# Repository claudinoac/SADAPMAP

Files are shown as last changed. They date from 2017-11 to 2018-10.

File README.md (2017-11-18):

# <h1> SADAMAP </h1>
<h2> Sistema de Aquisição de Dados para Análise de Materiais em Altas Pressões </h2>

<h3> Pré Requisitos de Instalação: </h3> 

<h4> Python 3.2+: </h4>
<ul> 
	<li> https://www.python.org/downloads/ </li>
</ul>
<h4>  </h4>
<h4> Bibliotecas Python: </h4>
<ul> 
	<li>  PyQtGraph: http://www.pyqtgraph.org/ </li>
	<li>  Numpy: http://www.numpy.org/ </li>
	<li>  PySerial: https://github.com/pyserial/pyserial </li>
	<li>  PyQt5: https://www.riverbankcomputing.com/software/pyqt/download5
</ul>

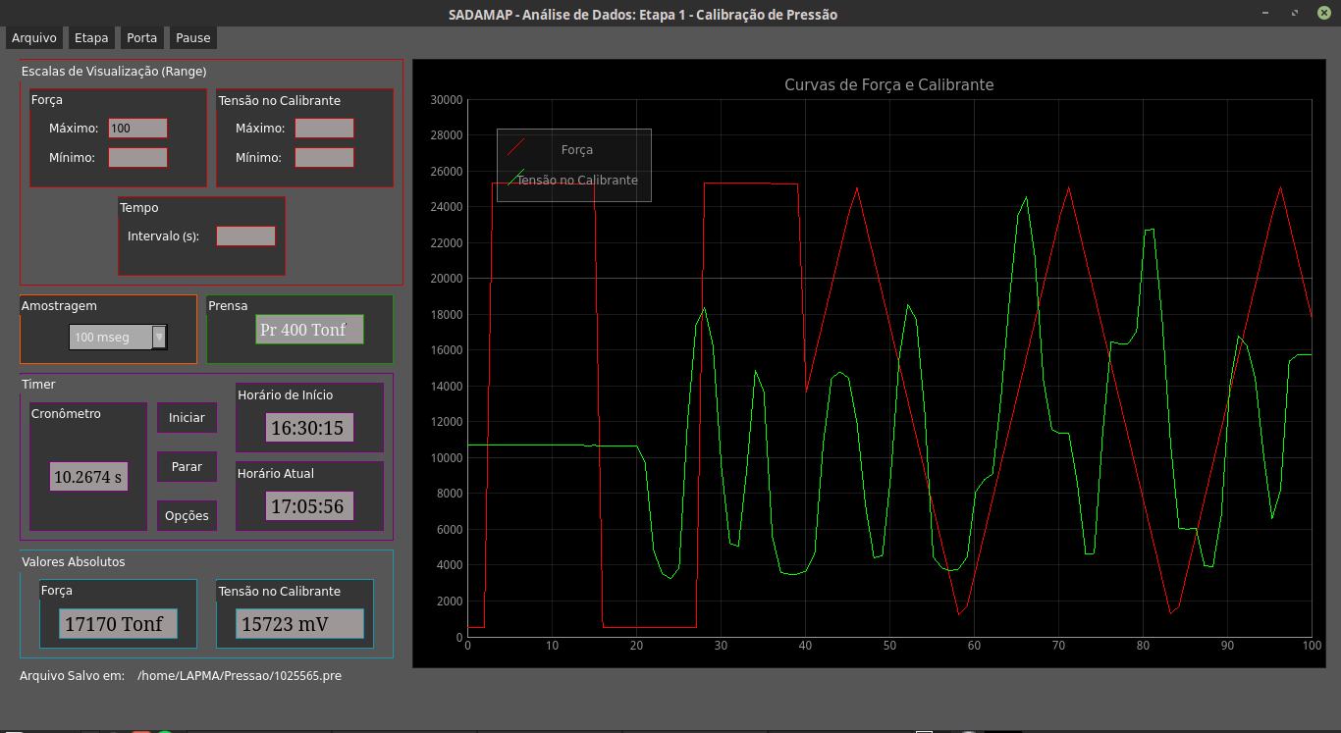
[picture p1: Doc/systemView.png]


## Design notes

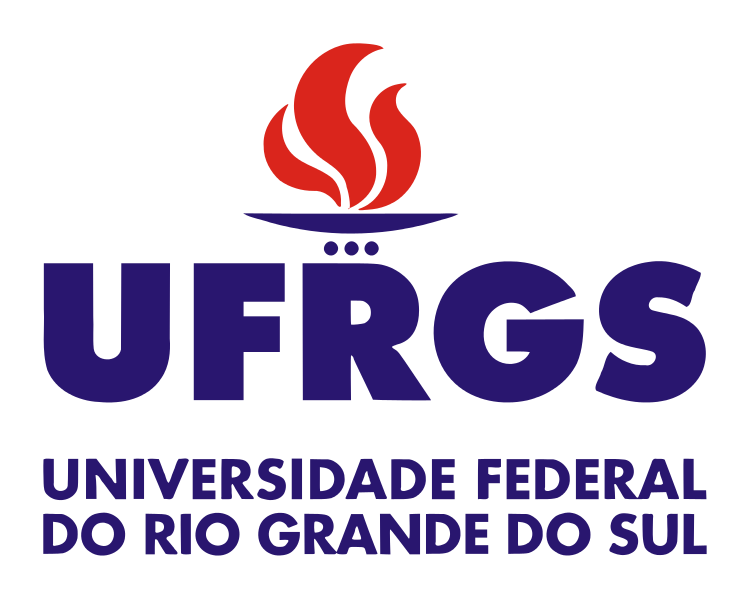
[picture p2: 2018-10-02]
Interface/Resources/750px-Ufrgs.svg.png

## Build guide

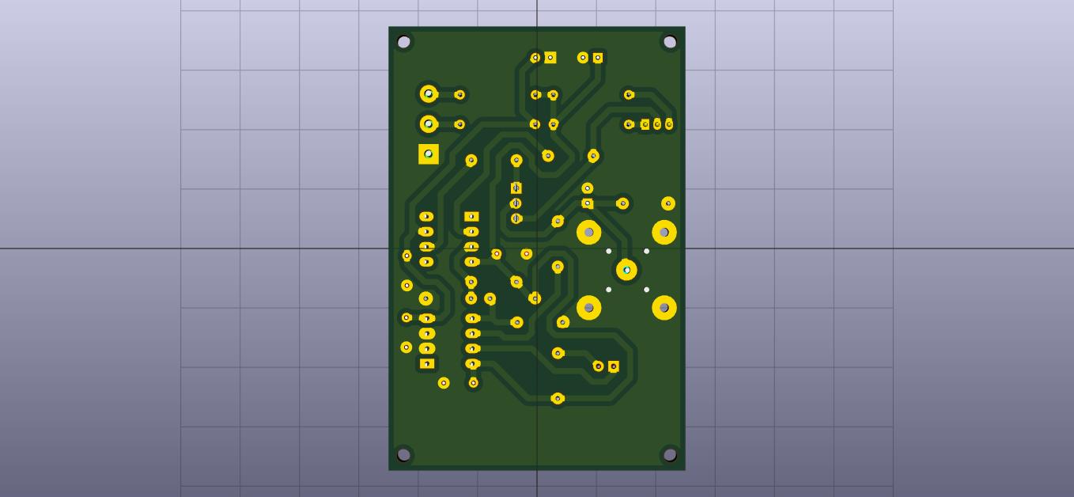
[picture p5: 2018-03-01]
Circuits/I_SOURCE/Fabrication Files/I_SOURCE_BACK.jpg

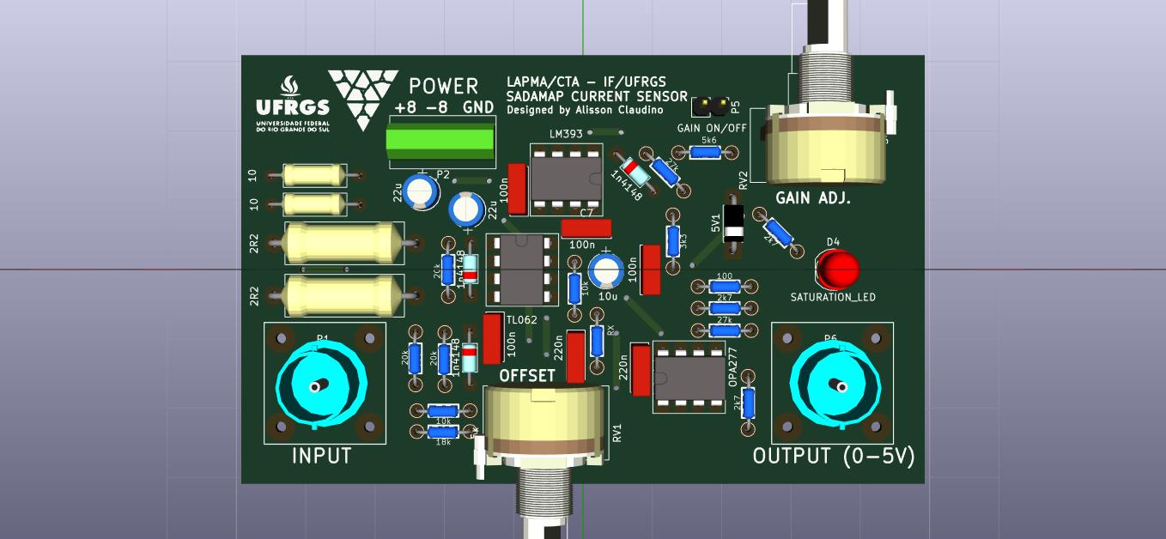
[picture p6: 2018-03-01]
Circuits/I_AMP/Fabrication Files/I_AMP_FRONT.jpg

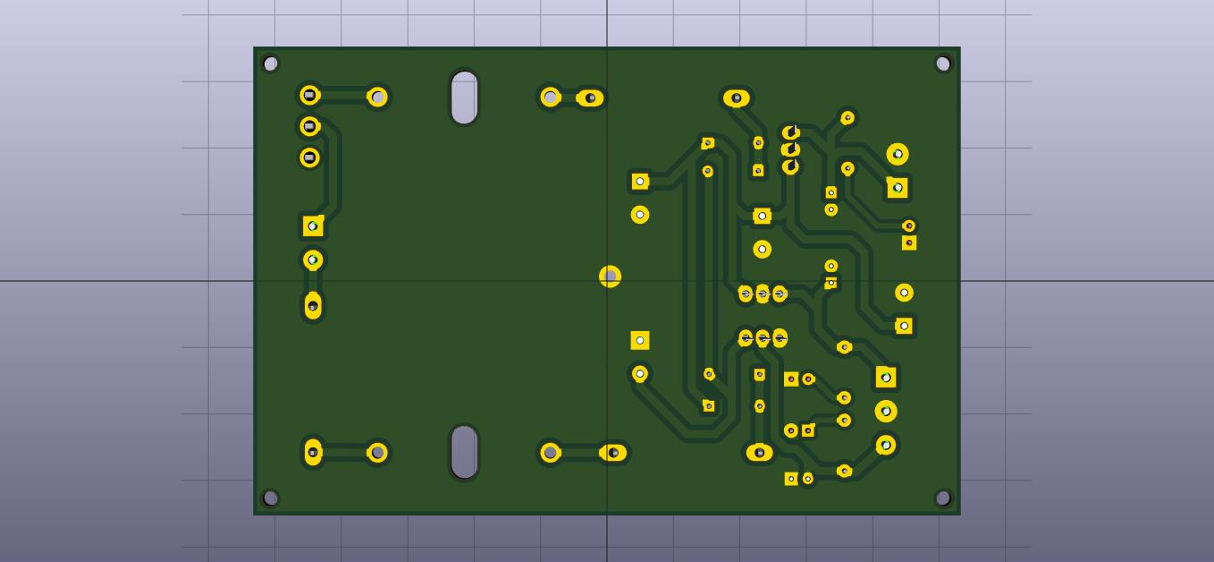
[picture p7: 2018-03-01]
Circuits/P_SUPPLY/Fabrication Files/P_SUPPLY_BACK.jpg

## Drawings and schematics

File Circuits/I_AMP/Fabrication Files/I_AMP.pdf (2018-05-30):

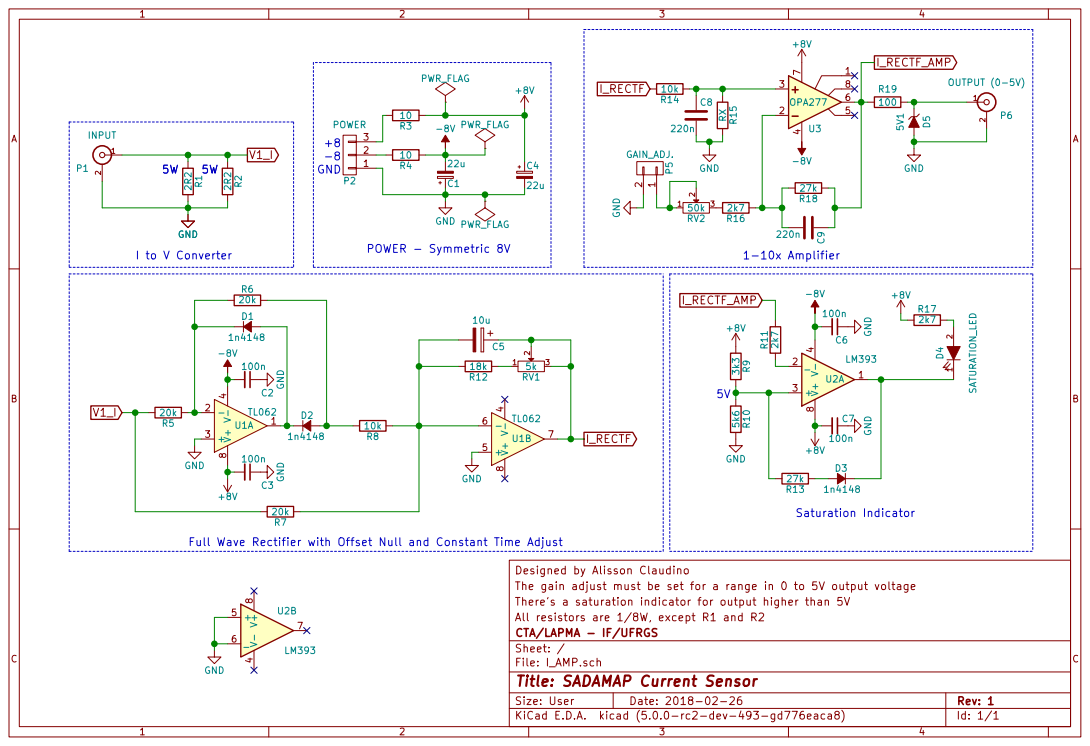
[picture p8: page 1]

Designed by Alisson Claudino GND

Full Wave Rectifier with Offset Null and Constant Time Adjust

The gain adjust must be set for a range in 0 to 5V output voltage
There's a saturation indicator for output higher than 5V
All resistors are 1/8W, except R1 and R2
File: I_AMP.sch Sheet: / CTA/LAPMA - IF/UFRGS

Id: 1/1 Title: SADAMAP Current Sensor

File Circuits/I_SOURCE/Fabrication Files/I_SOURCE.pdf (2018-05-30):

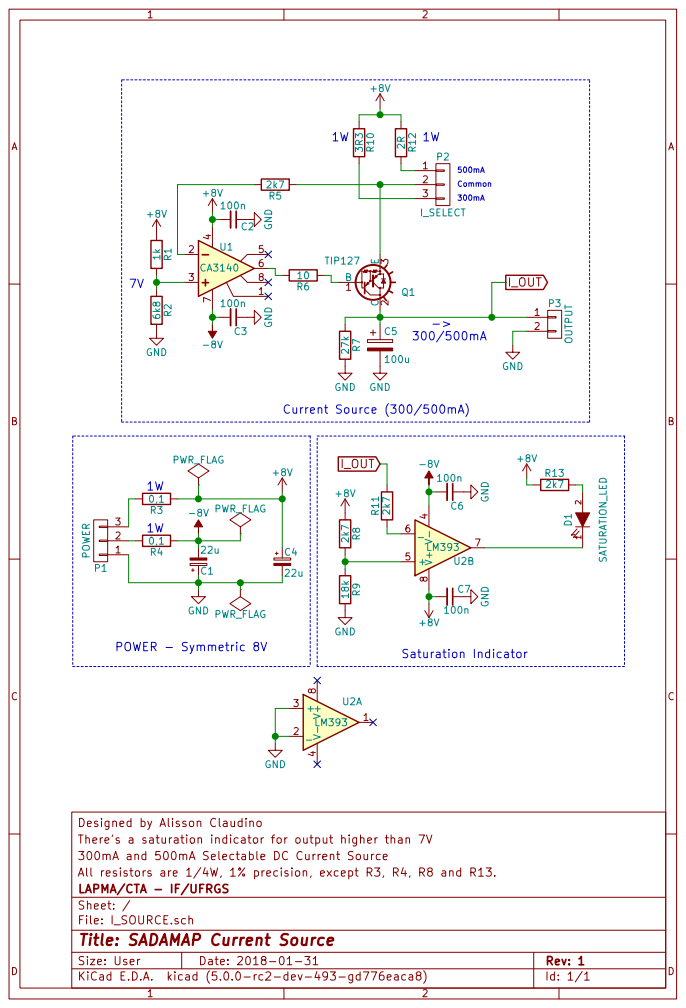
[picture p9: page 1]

Designed by Alisson Claudino
All resistors are 1/4W, 1% precision, except R3, R4, R8 and R13. 300mA and 500mA Selectable DC Current Source There's a saturation indicator for output higher than 7V

File: I_SOURCE.sch Sheet: / LAPMA/CTA - IF/UFRGS

Id: 1/1 Title: SADAMAP Current Source

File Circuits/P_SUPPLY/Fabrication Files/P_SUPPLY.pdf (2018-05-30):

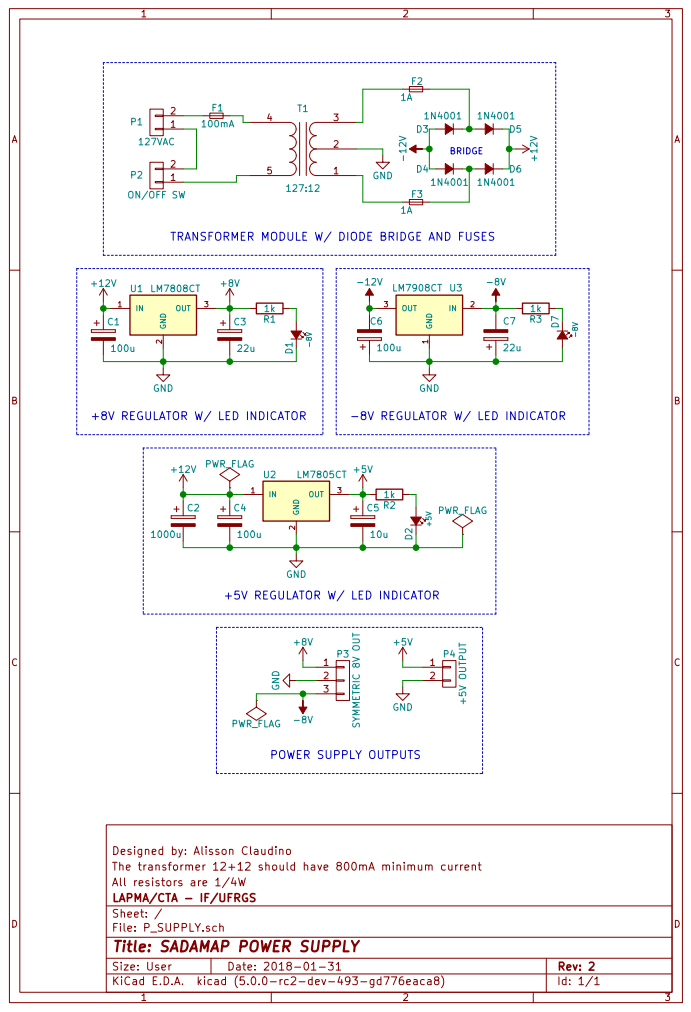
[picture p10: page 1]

1k TRANSFORMER MODULE W/ DIODE BRIDGE AND FUSES

The transformer 12+12 should have 800mA minimum current Designed by: Alisson Claudino

All resistors are 1/4W
File: P_SUPPLY.sch Sheet: / LAPMA/CTA - IF/UFRGS

Id: 1/1 Title: SADAMAP POWER SUPPLY

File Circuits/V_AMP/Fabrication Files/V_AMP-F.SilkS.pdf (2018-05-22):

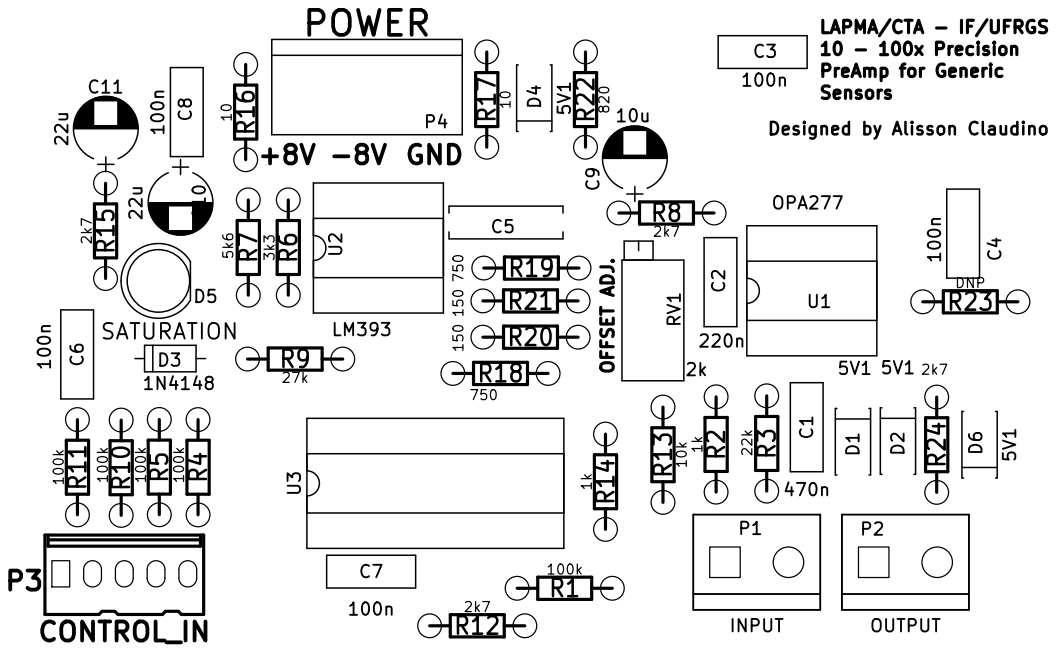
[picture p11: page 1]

LAPMA/CTA - IF/UFRGS
10 - 100x Precision PreAmp for Generic Sensors

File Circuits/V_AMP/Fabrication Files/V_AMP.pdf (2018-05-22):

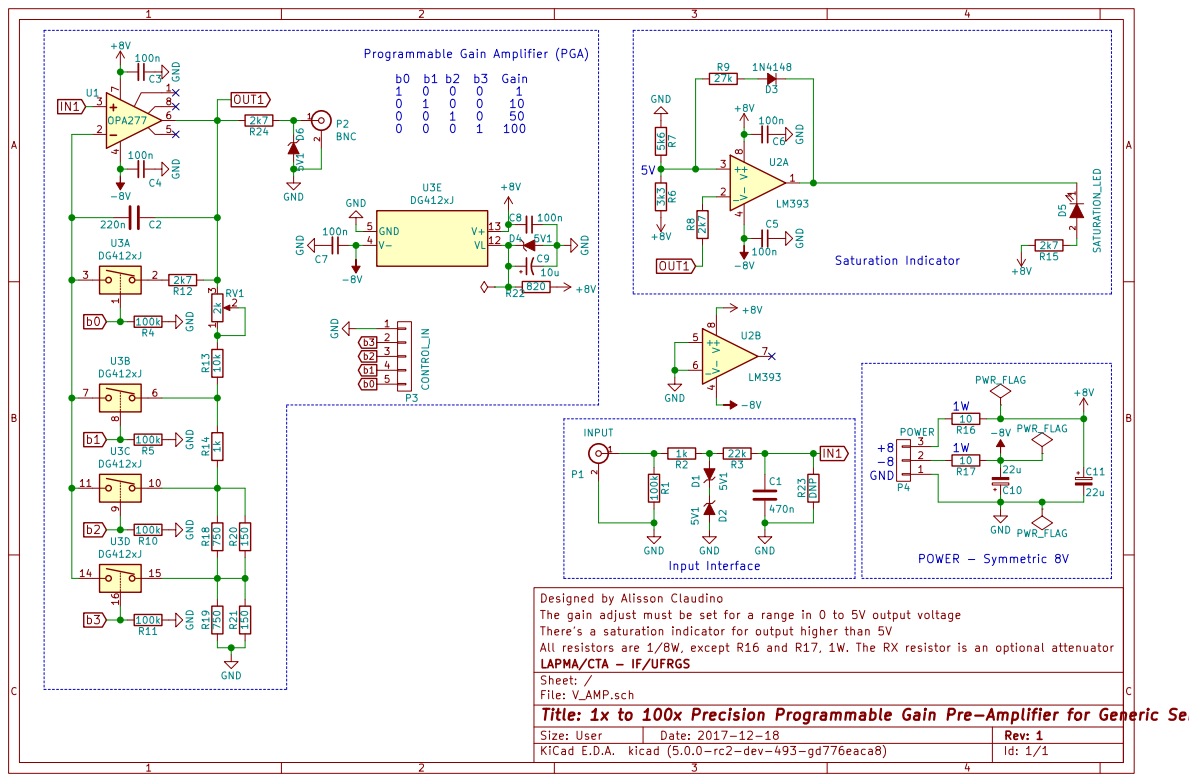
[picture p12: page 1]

Designed by Alisson Claudino
The gain adjust must be set for a range in 0 to 5V output voltage
There's a saturation indicator for output higher than 5V
All resistors are 1/8W, except R16 and R17, 1W. The RX resistor is an optional attenuator
LAPMA/CTA - IF/UFRGS
Sheet: /
File: V_AMP.sch
Title: 1x to 100x Precision Programmable Gain Pre-Amplifier for Generic Sensors
KiCad E.D.A. kicad (5.0.0-rc2-dev-493-gd776eaca8)

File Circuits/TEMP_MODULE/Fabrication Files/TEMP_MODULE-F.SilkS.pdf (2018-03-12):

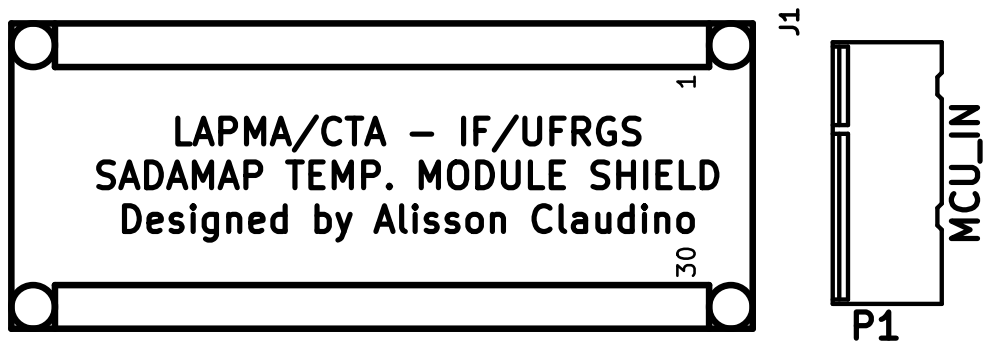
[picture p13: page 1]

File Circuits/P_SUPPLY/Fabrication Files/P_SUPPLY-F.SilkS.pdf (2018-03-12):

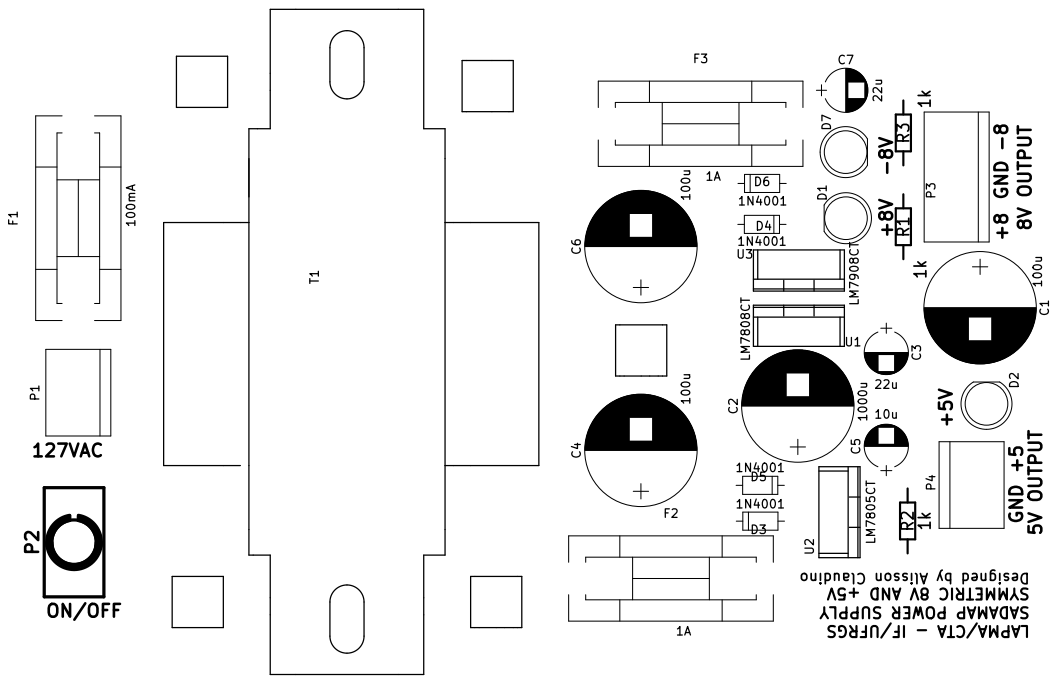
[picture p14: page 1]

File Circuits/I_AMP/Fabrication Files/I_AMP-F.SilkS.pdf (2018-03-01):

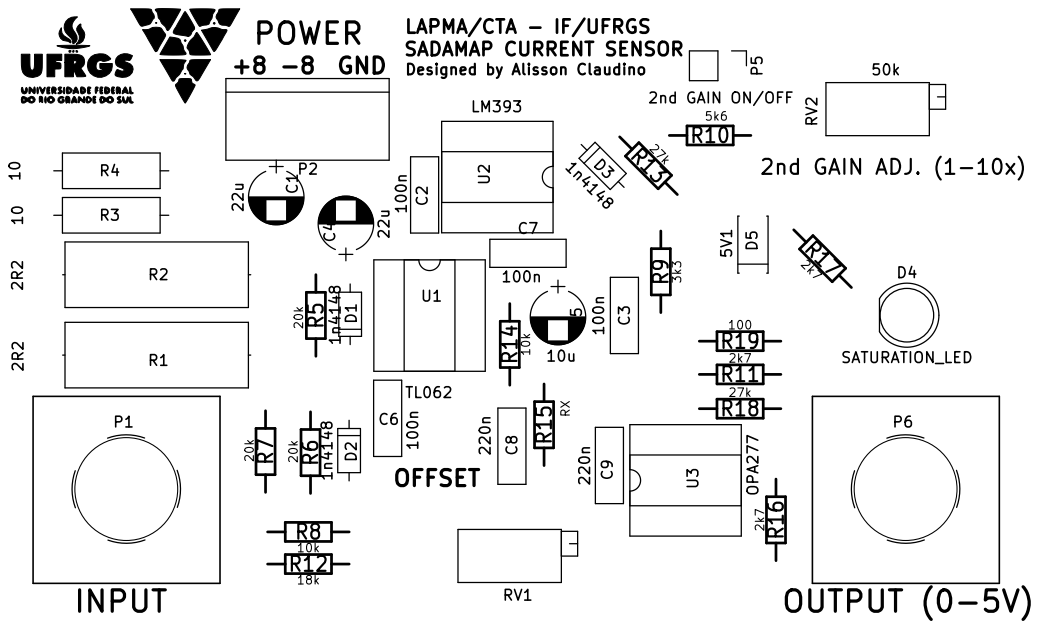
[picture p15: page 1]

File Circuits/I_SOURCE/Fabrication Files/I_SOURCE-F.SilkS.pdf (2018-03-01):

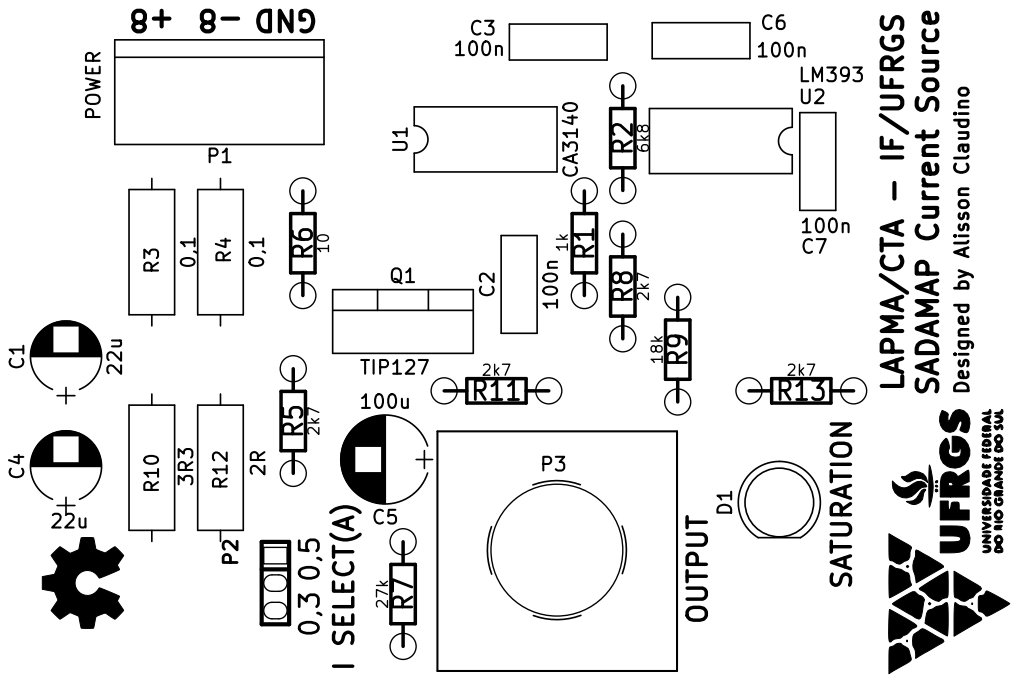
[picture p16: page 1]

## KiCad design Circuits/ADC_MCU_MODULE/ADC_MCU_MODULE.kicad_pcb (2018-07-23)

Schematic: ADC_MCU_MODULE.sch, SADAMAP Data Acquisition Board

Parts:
C1: 22u; C_Radial_D5_L6_P2.5
C2, C3, C4, C5, C6, C7, C8, C9: 100n; C_Rect_L7_W2.5_P5
J1: Arduino_Nano_Header; arduino_nano_header
P1: POWER; bornier2
P2, P3, P4, P5, P6, P7, P8, P9: BNC; bornier2
P10: TEMP_MODULE_OUT; kk100_22-23-2061
P11: V_AMP SEL CH-B; kk100_22-23-2051
P12: V_AMP SEL CH-A; kk100_22-23-2051
P13: V_AMP SEL CH-C; kk100_22-23-2051
R1: 10R; R_Axial_DIN0309_L9.0mm_D3.2mm_P12.70mm_Horizontal
R2, R3, R4, R5, R6, R7, R8, R9: 47k; RC03
U1, U2: ADS1115

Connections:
+5V: C1.1, J1.27 (5V), J1.30 (VIN), P10.2, R1.2, U1.1 (VCC), U2.1 (VCC), U2.5 (ADDR)
ADC1: C2.1, R2.1, U1.7 (A0)
ADC2: C5.1, R5.1, U1.8 (A1)
ADC3: C3.1, R3.1, U1.9 (A2)
ADC4: C4.1, R4.1, U1.10 (A3)
ADC5: C6.1, R6.1, U2.7 (A0)
ADC6: C7.1, R7.1, U2.8 (A1)
ADC7: C8.1, R8.1, U2.9 (A2)
ADC8: C9.1, R9.1, U2.10 (A3)
GND: C1.2, C2.2, C3.2, C4.2, C5.2, C6.2, C7.2, C8.2, C9.2, J1.4 (GND), J1.29 (GND), P1.1, P2.2 (Ext), P3.2 (Ext), P4.2 (Ext), P5.2 (Ext), P6.2 (Ext), P7.2 (Ext), P8.2 (Ext), P9.2 (Ext), P10.1, P11.1, P12.1, P13.1, U1.2 (GND), U1.5 (ADDR), U2.2 (GND)
MISO: J1.15 (D12/MISO), P10.4
MOSI: J1.14 (D11/MOSI), P10.5
unnamed: P1.2, R1.1
unnamed: P2.1 (In), R2.2
unnamed: P3.1 (In), R3.2
unnamed: P4.1 (In), R4.2
unnamed: P5.1 (In), R5.2
unnamed: P6.1 (In), R6.2
unnamed: P7.1 (In), R7.2
unnamed: P8.1 (In), R8.2
unnamed: P9.1 (In), R9.2
SCK: J1.16 (SCK/D13), P10.6
SCL: J1.24 (A5), U1.3 (SCL), U2.3 (SCL)
SDA: J1.23 (A4), U1.4 (SDA), U2.4 (SDA)
VA0: J1.19 (A0), P12.5
VA1: J1.20 (A1), P12.4
VA2: J1.21 (A2), P12.3
VA3: J1.22 (A3), P12.2
VB0: J1.5 (D2/INT0), P11.5
VB1: J1.6 (D3/INT1), P11.4
VB2: J1.7 (D4/T0), P11.3
VB3: J1.8 (D5/T1), P11.2
VC0: J1.9 (D6/AIN0), P13.5
VC1: J1.10 (D7/AIN1), P13.4
VC2: J1.11 (D8/ICP), P13.3
VC3: J1.12 (D9/0C1), P13.2
~CS: J1.13 (D10/SS), P10.3

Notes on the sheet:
INPUTS WITH ANTI-ALIASING LP FILTER
ADS1115 I2C MODULES The ADC_A has 0x48 I2C address and ADC_B, 0x49
POWER INPUT The 10R resistor is used as a fuse and the 22u capacitor is used as a filter
ARDUINO NANO MODULE
ADC_A
ADC_B
MAX31856 Temperature Module Header
Digital Voltage Amplifier Controls

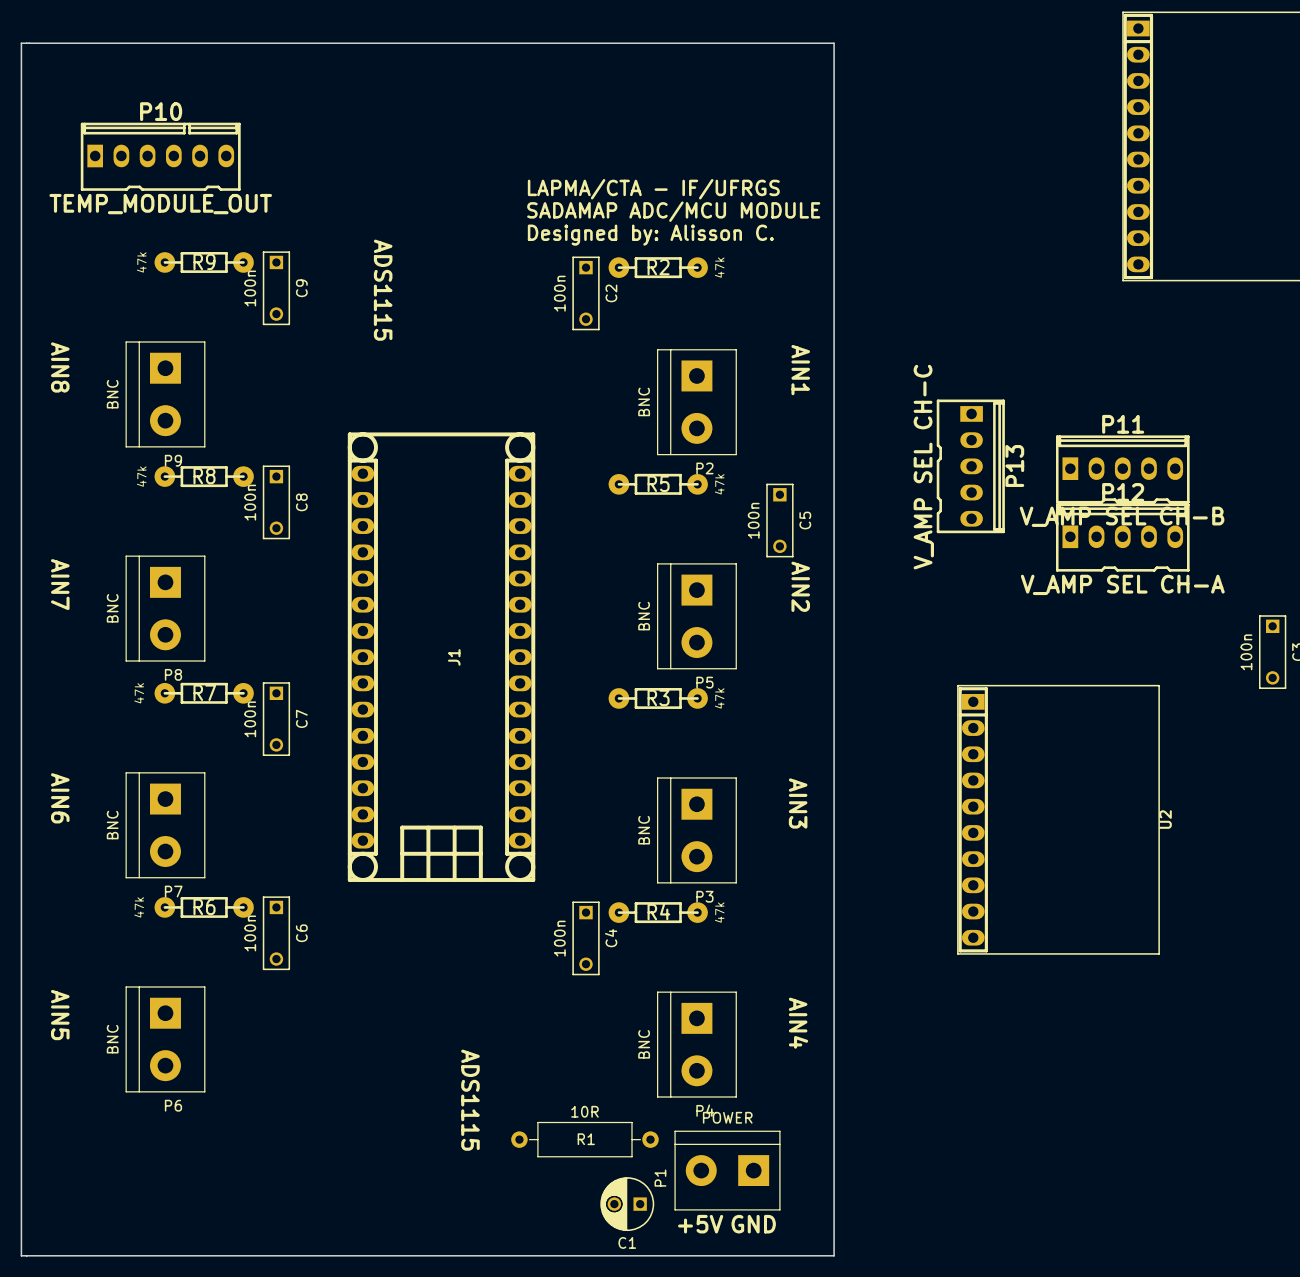
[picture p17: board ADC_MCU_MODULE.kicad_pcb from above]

Board: 2 copper layers, 78.8 x 117.5 mm, 34 parts (0 on the bottom side), 37 nets.

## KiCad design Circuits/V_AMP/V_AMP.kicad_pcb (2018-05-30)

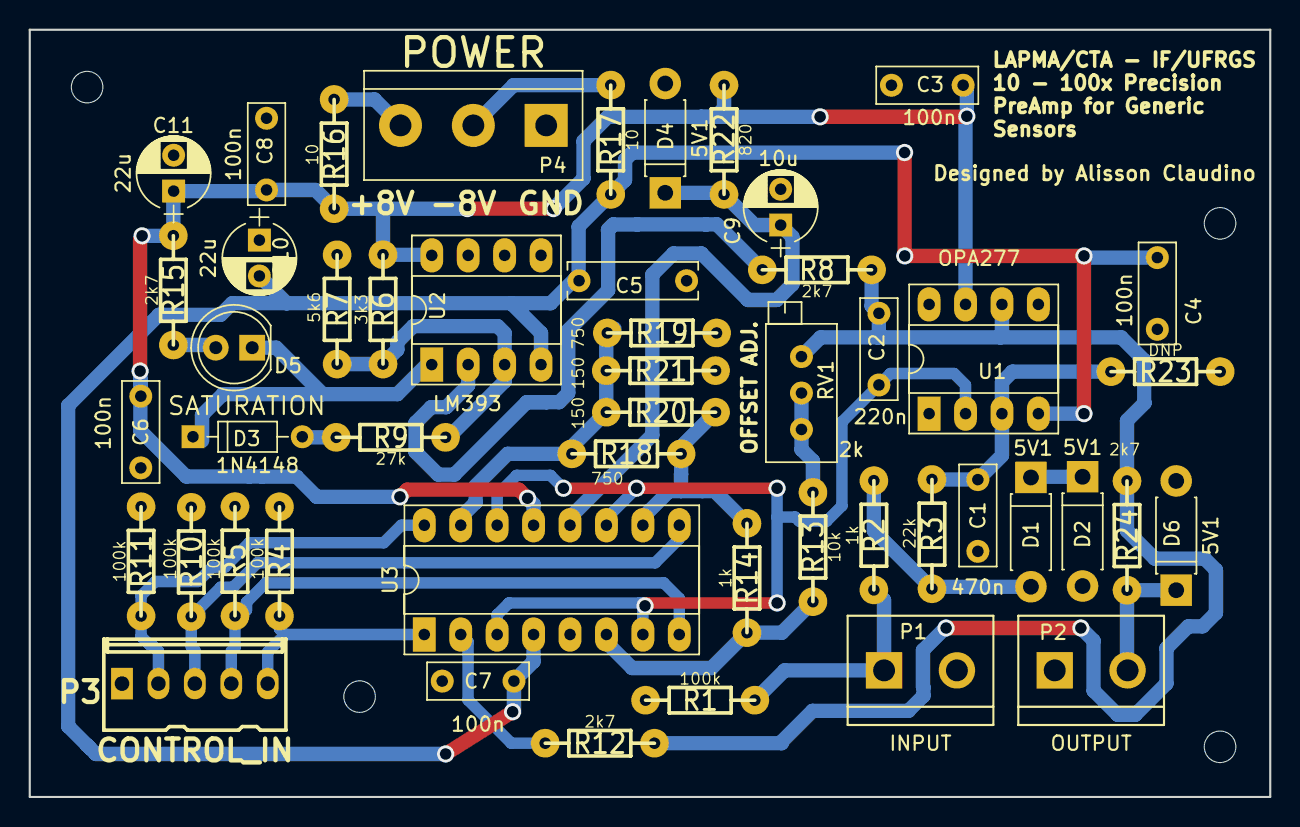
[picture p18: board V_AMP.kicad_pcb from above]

Board: 2 copper layers, 86.5 x 53.5 mm, 49 parts (0 on the bottom side), 27 nets.

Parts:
C1: 470n; C_Rect_L7.0mm_W2.5mm_P5.00mm
C2: 220n; C_Rect_L7.0mm_W2.5mm_P5.00mm
C3, C4, C6, C7, C8: 100n; C_Rect_L7.0mm_W2.5mm_P5.00mm
C5: 100n; C_Rect_L9.0mm_W2.5mm_P7.50mm_MKT
C9: 10u; CP_Radial_D5.0mm_P2.50mm
C10, C11: 22u; CP_Radial_D5.0mm_P2.50mm
D1, D2, D4, D6: 5V1; D_DO-41_SOD81_P7.62mm_Horizontal
D3: 1N4148; D_DO-35_SOD27_P7.62mm_Horizontal
D5: SATURATION; LED_D5.0mm
P1: INPUT; bornier2
P2: OUTPUT; bornier2
P3: CONTROL_IN; kk100_22-23-2051
P4: POWER; bornier3
R1, R4, R5, R10, R11: 100k; RC03
R2, R14: 1k; RC03
R3: 22k; RC03
R6: 3k3; RC03
R7: 5k6; RC03
R8, R12, R15, R24: 2k7; RC03
R9: 27k; RC03
R13: 10k; RC03
R16, R17: 10; RC03
R18, R19: 750; RC03
R20, R21: 150; RC03
R22: 820; RC03
R23: DNP; RC03
RV1: 2k; Potentiometer_Trimmer_Bourns_3296X
U1: OPA277; DIP-8_W7.62mm_Socket_LongPads
U2: LM393; DIP-8_W7.62mm_Socket_LongPads
U3: DG412xJ; DIP-16_W7.62mm_Socket_LongPads

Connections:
+8V: C3.2, C6.2, C8.2, C11.1, R6.1, R15.1, R16.1, R22.2, U1.7, U2.8, U3.13
-8V: C4.2, C5.2, C7.1, C10.2, R17.1, U1.4, U2.4, U3.4
GND: C1.2, C3.1, C4.1, C5.1, C6.1, C7.2, C8.1, C9.2, C10.1, C11.2, D2.2, D4.2, D6.2, P1.2, P2.1, P3.1, P4.1, R1.2, R4.1, R5.1, R7.2, R10.1, R11.1, R19.1, R21.1, R23.1, U2.5, U2.6, U3.5
IN1: C1.1, R3.1, R23.2, U1.3
unnamed: C2.2, U1.2, U3.3, U3.7, U3.11, U3.14
unnamed: C9.1, D4.1, R22.1, U3.12
unnamed: D1.1, D2.1
unnamed: D1.2, R2.1, R3.2
unnamed: D3.1, D5.1, U2.1
unnamed: D3.2, R9.1
unnamed: D5.2, R15.2
unnamed: D6.1, P2.2, R24.1
unnamed: P1.1, R1.1, R2.2
unnamed: P4.2, R17.2
unnamed: P4.3, R16.2
unnamed: R6.2, R7.1, R9.2, U2.3
unnamed: R8.1, U2.2
unnamed: R12.2, U3.2
unnamed: R13.1, R14.2, U3.6
unnamed: R13.2, RV1.1, RV1.2
unnamed: R14.1, R18.2, R20.2, U3.10
unnamed: R18.1, R19.2, R20.1, R21.2, U3.15
OUT1: C2.1, R8.2, R12.1, R24.2, RV1.3, U1.6
b0: P3.5, R4.2, U3.1
b1: P3.4, R5.2, U3.8
b2: P3.3, R10.2, U3.9
b3: P3.2, R11.2, U3.16

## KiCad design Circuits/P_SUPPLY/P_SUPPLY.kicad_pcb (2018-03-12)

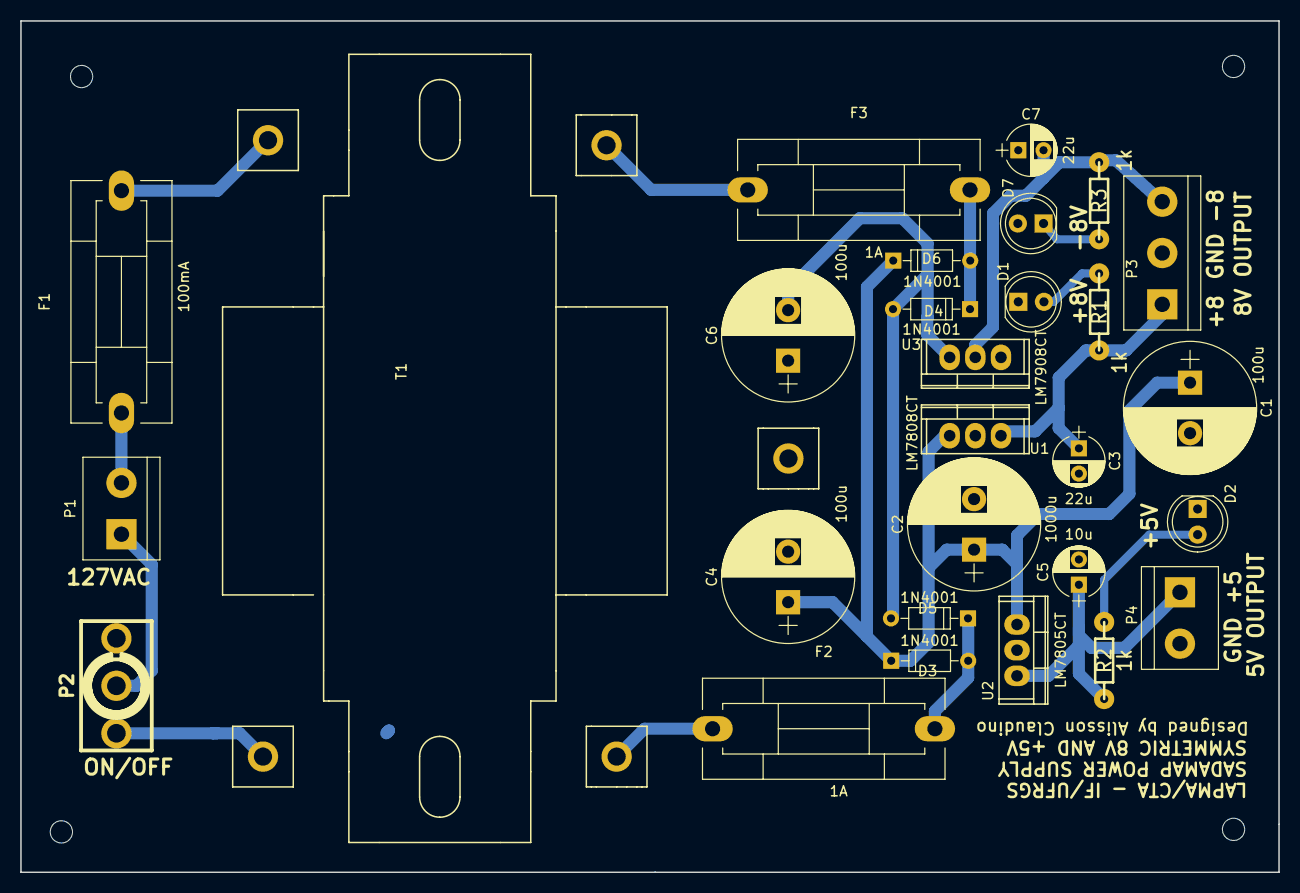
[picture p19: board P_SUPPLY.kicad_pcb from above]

Board: 2 copper layers, 124.5 x 84.2 mm, 28 parts (0 on the bottom side), 17 nets.

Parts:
C1, C4, C6: 100u; CP_Radial_D13.0mm_P5.00mm
C2: 1000u; CP_Radial_D13.0mm_P5.00mm
C3, C7: 22u; CP_Radial_D5.0mm_P2.50mm
C5: 10u; CP_Radial_D5.0mm_P2.50mm
D1: +8V; LED_D5.0mm
D2: +5V; LED_D5.0mm
D3, D4, D5, D6: 1N4001; D_DO-35_SOD27_P7.62mm_Horizontal
D7: -8V; LED_D5.0mm
F1: 100mA; Fuseholder5x20_horiz_SemiClosed_Casing10x25mm
F2, F3: 1A; Fuseholder5x20_horiz_SemiClosed_Casing10x25mm
P1: 127VAC; bornier2
P2: ON/OFF; switch_100sp5
P3: 8V OUTPUT; bornier3
P4: 5V OUTPUT; bornier2
R1, R2, R3: 1k; RC03
T1: 127:12; 12+12V_transformer_800mA-3T
U1: LM7808CT; TO-220
U2: LM7805CT; TO-220
U3: LM7908CT; TO-220

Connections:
+5V: C5.1, P4.1, R2.1, U2.3
+8V: C3.1, P3.1, R1.1, U1.3
+12V: C1.1, C2.1, C4.1, D5.1, D6.1, U1.1, U2.1
-8V: C7.2, P3.3, R3.1, U3.2
-12V: C6.2, D3.2, D4.2, U3.3
GND: C1.2, C2.2, C3.2, C4.2, C5.2, C6.1, C7.1, D1.1, D2.1, D7.2, P3.2, P4.2, T1.2, U1.2, U2.2, U3.1
unnamed: D1.2, R1.2
unnamed: D2.2, R2.2
unnamed: D3.1, D5.2, F2.2
unnamed: D4.1, D6.2, F3.2
unnamed: D7.1, R3.2
unnamed: F1.1, P1.2
unnamed: F1.2, T1.4
unnamed: F2.1, T1.3
unnamed: F3.1, T1.1
unnamed: P1.1, P2.2
unnamed: P2.1, T1.5

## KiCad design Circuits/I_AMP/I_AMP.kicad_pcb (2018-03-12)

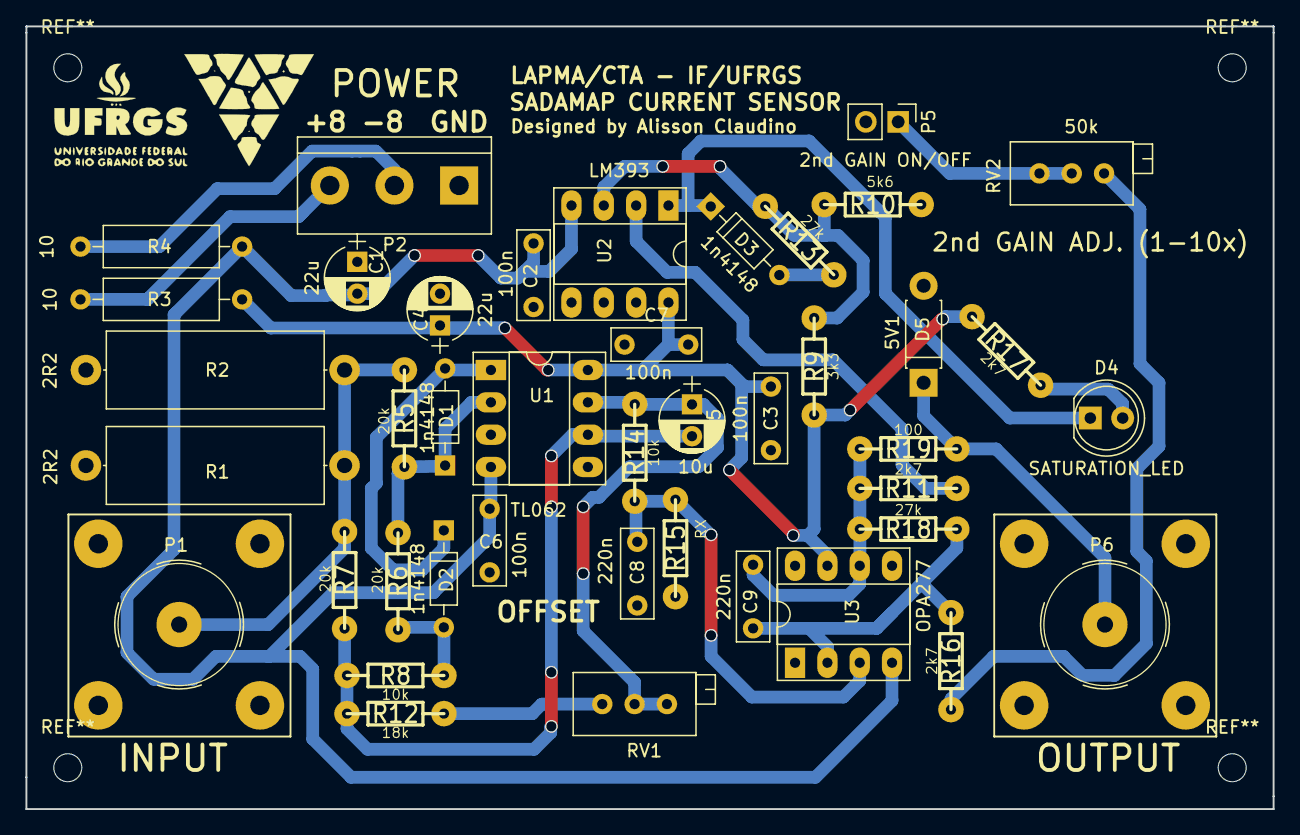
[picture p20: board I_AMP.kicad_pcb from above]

Board: 2 copper layers, 98.0 x 61.5 mm, 42 parts (0 on the bottom side), 23 nets.

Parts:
C1, C4: 22u; CP_Radial_D5.0mm_P2.50mm
C2, C3, C6, C7: 100n; C_Rect_L7.0mm_W2.5mm_P5.00mm
C5: 10u; CP_Radial_D5.0mm_P2.50mm
C8, C9: 220n; C_Rect_L7.0mm_W2.5mm_P5.00mm
D1, D2, D3: 1n4148; D_DO-35_SOD27_P7.62mm_Horizontal
D4: SATURATION_LED; LED_D5.0mm
D5: 5V1; D_DO-41_SOD81_P7.62mm_Horizontal
P1: INPUT; bnc-ci
P2: POWER; bornier3
P5: 2nd GAIN ON/OFF; Pin_Header_Straight_1x02_Pitch2.54mm
P6: OUTPUT; bnc-ci
R1, R2: 2R2; R_Axial_DIN0617_L17.0mm_D6.0mm_P20.32mm_Horizontal
R3, R4: 10; R_Axial_DIN0309_L9.0mm_D3.2mm_P12.70mm_Horizontal
R5, R6, R7: 20k; RC03
R8, R14: 10k; RC03
R9: 3k3; RC03
R10: 5k6; RC03
R11, R16, R17: 2k7; RC03
R12: 18k; RC03
R13, R18: 27k; RC03
R15: RX; RC03
R19: 100; RC03
RV1: 5k; Potentiometer_Trimmer_Bourns_3296X
RV2: 50k; Potentiometer_Trimmer_Bourns_3296X
U1: TL062; DIP-8_W7.62mm_Socket_LongPads
U2: LM393; DIP-8_W7.62mm_Socket_LongPads
U3: OPA277; DIP-8_W7.62mm_Socket_LongPads

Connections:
+8V: C3.2, C4.1, C7.2, R3.1, R9.1, R17.1, U1.8, U2.8, U3.7
-8V: C1.2, C2.2, C6.2, R4.1, U1.4, U2.4, U3.4
GND: C1.1, C2.1, C3.1, C4.2, C6.1, C7.1, C8.2, D5.2, P1.2, P2.1, P5.2, P6.2, R1.2, R2.2, R10.2, R15.2, U1.3, U1.5, U2.5, U2.6
I_RECTF: C5.1, R14.2, RV1.2, RV1.3, U1.7
I_RECTF_AMP: C9.1, R11.2, R18.1, R19.2, U3.6
unnamed: C5.2, R7.1, R8.1, R12.2, U1.6
unnamed: C8.1, R14.1, R15.1, U3.3
unnamed: C9.2, R16.1, R18.2, U3.2
unnamed: D1.1, R5.1, R6.2, U1.2
unnamed: D1.2, D2.1, U1.1
unnamed: D2.2, R6.1, R8.2
unnamed: D3.1, D4.1, U2.1
unnamed: D3.2, R13.1
unnamed: D4.2, R17.2
unnamed: D5.1, P6.1, R19.1
unnamed: P2.2, R4.2
unnamed: P2.3, R3.2
unnamed: P5.1, RV2.1, RV2.2
unnamed: R9.2, R10.1, R13.2, U2.3
unnamed: R11.1, U2.2
unnamed: R12.1, RV1.1
unnamed: R16.2, RV2.3
V1_I: P1.1, R1.1, R2.1, R5.2, R7.2

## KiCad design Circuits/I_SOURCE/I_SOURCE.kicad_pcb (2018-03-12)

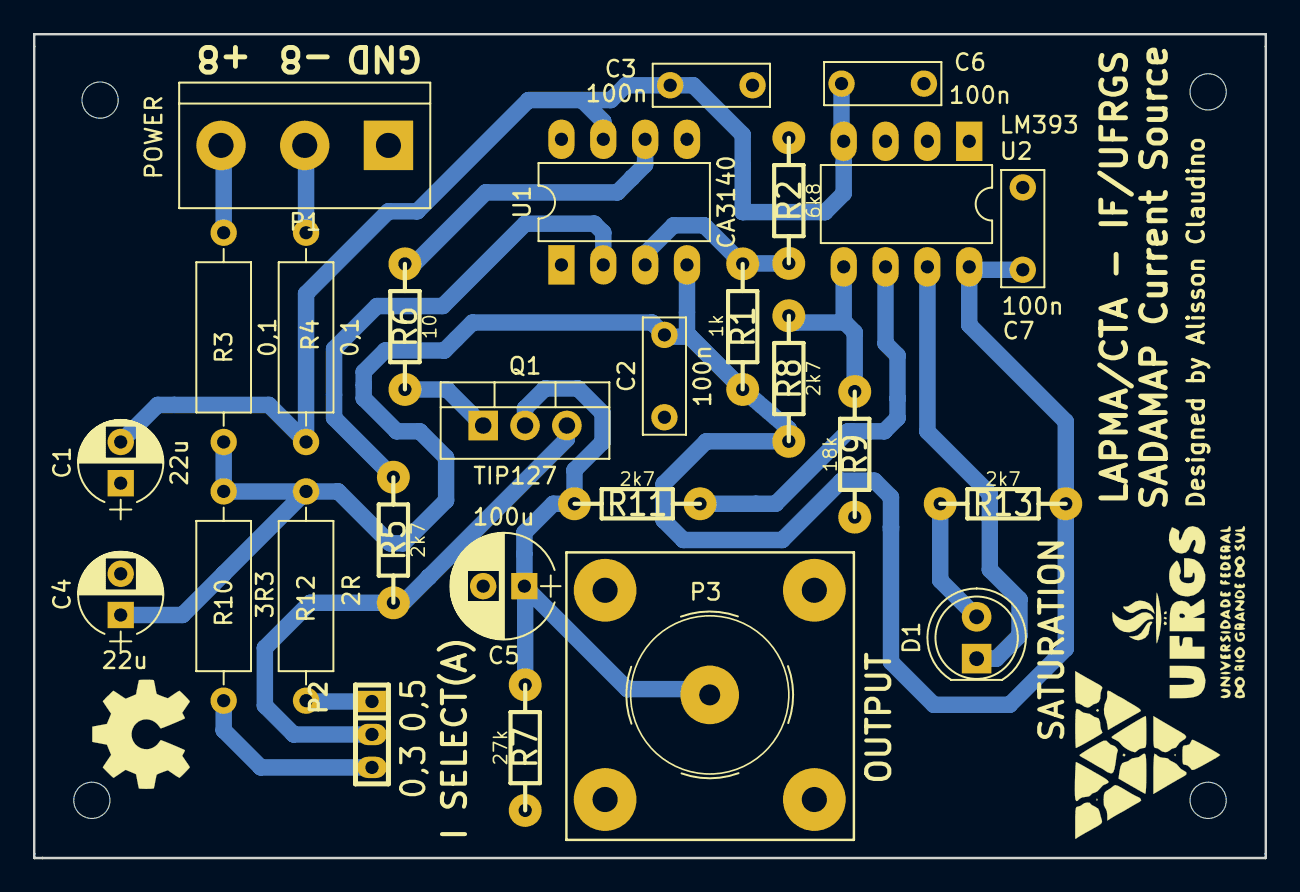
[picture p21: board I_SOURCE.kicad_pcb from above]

Board: 2 copper layers, 74.8 x 50.0 mm, 27 parts (0 on the bottom side), 17 nets.

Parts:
C1, C4: 22u; CP_Radial_D5.0mm_P2.50mm
C2, C3, C6, C7: 100n; C_Rect_L7.0mm_W2.5mm_P5.00mm
C5: 100u; CP_Radial_D6.3mm_P2.50mm
D1: SATURATION; LED_D5.0mm
P1: POWER; bornier3
P2: I_SELECT; pin_strip_2mm_3
P3: OUTPUT; bnc-ci
Q1: TIP127; TO-220_Vertical
R1: 1k; RC03
R2: 6k8; RC03
R3, R4: 0,1; R_Axial_DIN0309_L9.0mm_D3.2mm_P12.70mm_Horizontal
R5, R8, R11, R13: 2k7; RC03
R6: 10; RC03
R7: 27k; RC03
R9: 18k; RC03
R10: 3R3; R_Axial_DIN0309_L9.0mm_D3.2mm_P12.70mm_Horizontal
R12: 2R; R_Axial_DIN0309_L9.0mm_D3.2mm_P12.70mm_Horizontal
U1: CA3140; DIP-8_W7.62mm_LongPads
U2: LM393; DIP-8_W7.62mm_LongPads

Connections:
+8V: C2.2, C4.1, C7.2, R1.1, R3.1, R8.1, R10.1, R12.1, R13.1, U1.4, U2.8
-8V: C1.2, C3.2, C6.2, R4.1, U1.7, U2.4
GND: C1.1, C2.1, C3.1, C4.2, C5.2, C6.1, C7.1, P1.1, P3.2, R2.2, R7.2, R9.2, U2.2, U2.3
I_OUT: C5.1, P3.1, Q1.2, R7.1, R11.2
unnamed: D1.1, U2.7
unnamed: D1.2, R13.2
unnamed: P1.2, R4.2
unnamed: P1.3, R3.2
unnamed: P2.1, R12.2
unnamed: P2.2, Q1.3, R5.1
unnamed: P2.3, R10.2
unnamed: Q1.1, R6.1
unnamed: R1.2, R2.1, U1.3
unnamed: R5.2, U1.2
unnamed: R6.2, U1.6
unnamed: R8.2, R9.1, U2.5
unnamed: R11.1, U2.6

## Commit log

2017-07-18 Adicionado algoritmo de amostragem constante
2017-09-19 EDIT: Organização de arquivos de código
2017-09-19 Adicionado código de leitura do ADC e impressão na serial
2017-09-19 Adicionadas as dependências de Instalação
2017-10-03 Mudança de biblioteca gráfica para PyQtGraph na interface
2017-10-04 Corrigido Erro de escala de eixos
2017-10-07 Adição do gráfico em um QGraphicsScene para torná-lo um Widget
2017-10-13 Atualizado o README.md para o novo nome do projeto
2017-10-25 Transcrição do código para orientação a objeto
2017-10-25 Adição dos códigos para o ADS1115 com leitura dos 4 canais
2017-10-26 Configuração do ADC e da interface para 4 canais simultâneos
2017-10-27 Adição de mais 4 sensores, dois ADCs, 8 canais em simultâneo
2017-10-30 Adicionados arquivos de layout de interface
2017-11-10 Funcionando o código separado em classes, nomeação de componentes gráficos e alteração dinâmica de escala de gráficos
2017-11-14 Separação de classes em arquivos e config. serial na interface
2017-11-16 Bug na mudança de escala
2017-11-18 Adição da Pasta de Arquivos de Documentação
2017-11-24 Construida a interface da calibração de temperatura
2017-11-24 Ajustada escala de tempo de acordo com a amostragem
2017-11-24 Adicionado arquivo da classe de manipulação de arquivos
2017-11-24 Modificado o nome da main para o nome do projeto
2017-11-27 Adicionada Classe abstrata Inter faceTimer para gerenciar os timers da interdace
2017-12-01 Feita a documentação da classe Graph e generalizada a mesma para n curvas
2017-12-01 Ajuste de escalas de curvas configurado e atualização da documentação
2017-12-01 Adição de avisos em caso de dados inválidos na atualização
2017-12-05 Engine adaptado para novo modelo da classe Graph
2017-12-05 ADD: Amplificadores de Corrente e Tensão
    [I_AMP.kicad_pcb, I_AMP.sch, V_AMP.kicad_pcb, V_AMP.sch]
2017-12-11 Adicionada fonte de corrente e corrigido sensor de corrente
    [I_AMP.sch, I_SOURCE.kicad_pcb, I_SOURCE.sch]
2017-12-15 ADD: Schematic Documentation
    [I_AMP.sch, I_SOURCE.sch, V_AMP.sch]
2017-12-18 Complete PCB Design of the PreAmp 10-100
    [V_AMP.kicad_pcb, V_AMP.sch]
2018-01-19 Added full schematics and power supply
    [I_AMP.sch, I_SOURCE.kicad_pcb, I_SOURCE.sch, P_SUPPLY.kicad_pcb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]
2018-01-29 ADD: Complete Power Supply SCH+PCB
    [P_SUPPLY.kicad_pcb, P_SUPPLY.sch]
2018-01-31 EDIT: Page SETUP
    [P_SUPPLY.kicad_pcb, V_AMP.kicad_pcb]
2018-01-31 ADD: Power Supply Board 3D Visualizations
2018-01-31 EDIT: Reorganize Files
    [I_AMP.kicad_pcb, I_AMP.sch, I_SOURCE.kicad_pcb, I_SOURCE.sch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]
2018-01-31 EDIT: Reorganizing Files
    [I_AMP.kicad_pcb, I_AMP.sch, I_SOURCE.kicad_pcb, I_SOURCE.sch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]
2018-01-31 ADD: Current Source full PCB design
    [I_SOURCE.kicad_pcb, I_SOURCE.sch]
2018-01-31 ADD: Holes in Power Supply PCB
    [P_SUPPLY.kicad_pcb, P_SUPPLY.sch]
2018-01-31 EDIT: Shunt power resistors for alimentation input
    [V_AMP.kicad_pcb]
2018-02-26 ADD: Current Amplifier Complete PCB Design
    [I_AMP.kicad_pcb, I_AMP.sch]
2018-02-26 EDIT: Correction of some jumpers
    [I_AMP.kicad_pcb]
2018-02-28 ADD: Complete SCH+PCB of the ADC/MCU Board
    [ADC_MCU_MODULE.kicad_pcb, ADC_MCU_MODULE.sch]
2018-03-01 ADD: Complete Current Source SCH+PCB w/ Gerbers
    [I_SOURCE-B.Cu.gbr, I_SOURCE-Edge.Cuts.gbr, I_SOURCE-F.Cu.gbr, I_SOURCE.drl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]
2018-03-01 EDIT: Update F.Silks and BOM of the Current Source Board
2018-03-01 EDIT: Power Supply PCB Correction and ADD BOM
    [P_SUPPLY.kicad_pcb]
2018-03-01 ADD: Current Sensor Fabrication Files
    [I_AMP-B.Cu.gbr, I_AMP-Edge.Cuts.gbr, I_AMP-F.Cu.gbr, I_AMP.drl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]
2018-03-12 ADD: Current Source fabrication files
    [I_SOURCE-B.Cu.gbr, I_SOURCE-Edge.Cuts.gbr, I_SOURCE-F.Cu.gbr, I_SOURCE.drl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]
2018-03-12 ADD: ADC/MCU Module Fabrication Files
    [ADC_MCU_MODULE-B.Cu.gbr, ADC_MCU_MODULE-Edge.Cuts.gbr, ADC_MCU_MODULE-F.Cu.gbr, ADC_MCU_MODULE.drl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]
2018-03-12 EDIT: Correction of the Current Sensor board
    [I_AMP-B.Cu.gbr, I_AMP-Edge.Cuts.gbr, I_AMP-F.Cu.gbr, I_AMP.drl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]
2018-03-12 ADD: Power Supply Fabrication Files
    [P_SUPPLY-B.Cu.gbr, P_SUPPLY-Edge.Cuts.gbr, P_SUPPLY-F.Cu.gbr, P_SUPPLY.drl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]
2018-03-12 ADD: Temperature Sensor Module SCH + PCB + Fabrication Files
    [TEMP_MODULE-B.Cu.gbr, TEMP_MODULE-Edge.Cuts.gbr, TEMP_MODULE-F.Cu.gbr, TEMP_MODULE.drl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]
2018-03-12 EDIT: Some Modifications in the General Amplifier
    [V_AMP.kicad_pcb, V_AMP.sch]
2018-04-13 EDIT: V_AMP is a PGA now
    [V_AMP.sch]
2018-05-22 ADD: V_AMP pcb design
    [I_AMP-B.Cu.gbr, I_AMP-Edge.Cuts.gbr, I_AMP-F.Cu.gbr, I_AMP.drl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]
2018-05-22 ADD: V_AMP Fabrication Files
    [V_AMP-B.Cu.gbr, V_AMP-Edge.Cuts.gbr, V_AMP-F.Cu.gbr, V_AMP.drl]
2018-06-19 EDIT: ADC_MCU new schematic
    [ADC_MCU_MODULE.kicad_pcb, ADC_MCU_MODULE.sch]
2018-07-23 ADD: ADC_MCU New Schematic
    [ADC_MCU_MODULE-B.Cu.gbr, ADC_MCU_MODULE-Edge.Cuts.gbr, ADC_MCU_MODULE-F.Cu.gbr, ADC_MCU_MODULE.drl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]
2018-10-04 ADD: Temperature Calibration Access via Main Window
